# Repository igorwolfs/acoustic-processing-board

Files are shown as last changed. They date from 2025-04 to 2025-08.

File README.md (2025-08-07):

# acoustic-processing-hw
Repository for the main FPGA-processing board of my acoustic characterization device.

## Design goal
The goal of the board is to 
1. Measure analog signals amplified by a [pre-amplifier board](https://github.com/igorwolfs/acoustic-preamp-hw) for signals picked up from the piezo, at frequencies between 0.1 and 10 MHz. These analog signals are stored in RAM after measurement, processed on the FPGA and passed on.
2. Drive PWM signals for a [single-phase inverter-board](https://github.com/igorwolfs/acoustic-piezodriver-hw) connected to a piezo-element.

## Design constraints
Apart from technical constraints such as sampling rate (> 20 MHz), transfer / processing speed (10-bit x 35 MHz), etc... The main design constraint was keeping the price as low as possible.

## Stackup / Routing
6-layer stackup (JLC06161H-3313) with 
- L1, L6: controlled impedance layers.
	- 50 Ohm non-coplanar microstrip: 
		- TL Width (W): 0.157 mm 
		- Spacing between conductors: 2-3 x W
	- 100 Ohm differential non-coplanar
		- TL width (W): 0.122 mm
		- Diff-pair spacing: 0.2032 mm
		- Conductor spacing: 2-3 x W
- L4: power plane:
	- +2V5 Auxiliary FPGA voltage
	- +1V35 LPDDR3 voltage
	- +1V2 ETH voltage
	- +3V3 digital
	- +3V3 analog
- L2, L3, L5: GND planes
	- L2 (L1 reference)
	- L3 (L4 reference)
	- L5 (L6 reference)

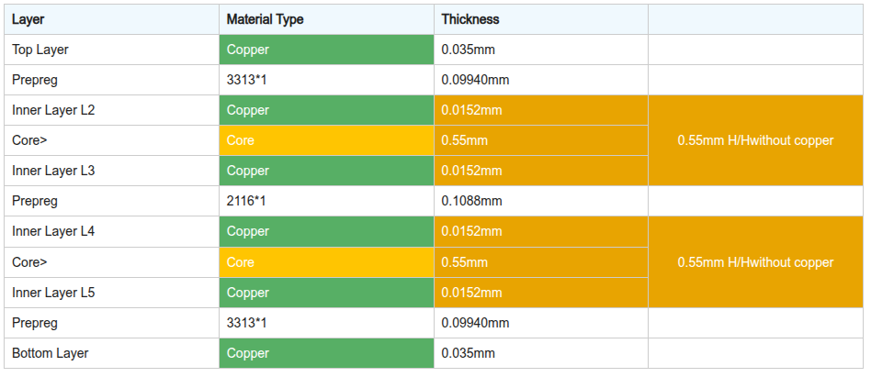
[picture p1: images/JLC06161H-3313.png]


### Rationale
Main reason for choosing a 6-layer over an 8-layer stack-up was price. Keeping LPDDR3-traces at appropriate impedance and matching delays proved to be a challenge with this layer count. Outcome to be judged after bringup.

## Main IC's
- Lattice EC5U-FPGA, with 25k LUT's.
- LPDDR3-RAM
- USB 33200-PHY (ULPI-bus)
- Ethernet PHY (RGMII interface)
- Analog frontend with MS9280 ADC in diff-mode, (fs <=35 MHz).

### Routing / Selection Rationale
#### Lattice ECP5U
The Lattice ECP5U was the best price-quality in terms of computing power. 

With a max CLK frequency of about 400 MHz it can operate around the lowest DDR3 speed class.

#### KSZ9031RN-Ethernet
Often used in open-source boards together with the ECP5U.

- RGMII interface operating at 125 MHz
- Differential pair needs to be tightly matched, offset calibration between pairs is performed.
- 4-pair RJ45 with intergrated magnetics (HR911130A)

#### Micron-DDR3 PHY
Anticipated was that around lower DDR3-speed classes (300 MHz, $\lambda = \frac{c}{300e6 * \sqrt{4.1}} = 50 cm$), delay-matching becomes less of an issue and higher ECP5U rise and fall times increase tolerance margin for the 50 ohm single-ended / 100 ohm differential impedance requirements.

- CMD-CTRL-bus 
	- signals led through vias twice.
	- CK+/- 42 mm
	- CMD/CTRL BUS signals kept around 35 mm (between 34-37 mm)
- DQU-group 
	- led through vias twice.
	- UDQS+/-: 21.7 mm
	- Data-signals kept within 1.5 mm
- DQL-group
	- signals kept on the first layer only.
	- LDQS+/-: 19.85 mm
	- Data-signals kept within 1.5 mm

 > References: [Orangecrab Board](https://github.com/orangecrab-fpga/orangecrab-hardware), Section 3.18 Lattice FPGA-DS-02012-3.2, [Micron DDR3 SDRAM](https://jlcpcb.com/api/file/downloadByFileSystemAccessId/8588894245961019392) table 58

#### USB3300-EZK
- ULPI-bus operating at 60 MHz
	- Traces were [delay-matched](docs/layout/USB/routing.md).
	- Impedance matched to 50 ohms.
- 2 Schmitt triggers were added for read-out of CC-line voltage to determine current USB PD capacity.

#### MS9280 ADC
Sampling rate > 2 times Nyquist, purchasing price was less than 1 $.

#### ADC RJ45 connectors + switch

2 RJ45 connectors meant to transfer analog signals attached with a switch. A comparison will be made for measuring analog signals between
- An RJ45 connector with internal magnetics.
- An RJ45 connector without magnetics, and with external blocking capacitors.
	- Capacitors might need to be changed, to stay out of S.R.F territory and limit phase-shift between differential signals.

#### W25Q128JVS SPI
2 external 128 MBit SPI IC's connected
- One to flash the ECP5U bitstream.
- One to flash firmware used in case of a soft-core CPU configured in the FPGA-fabric.

#### Other
More info on routing can be found in the (rather chaotic) [layout folder](docs/layout/) and [component selection folder](docs/schematic/component_selection/).

Simulations for ADI-devices can be found inside [ltspice-folder](simulations/ltspice/), TI-related sims can be found in the [TI-folder](simulations/TINA/)

## Booting
### Loading Bitstream 
2 possible ways of loading the bitstream of the ECP5U
- The JTAG-PMOD connector
- Flashing the external 128 MBit SPI connected to the startup MSPI of the ECP5U.

## Reviews
### Reddit
The first iteration of the design was placed on [reddit for review](https://www.reddit.com/r/PrintedCircuitBoard/comments/1m0hude/schematic_review_request_ecp5ufpga_board_with_hs/).

The initial design included longer trace-lengths to the DDR-PHY to achieve better delay and impedance matching. It was deemed that for the given stackup, sacrificing delay-budget and inter-trace distance wasn't worth the increase in trace lengths at those frequencies.

<table>
  <tr>
    <th>Before</th>
    <th>After</th>
  <tr>
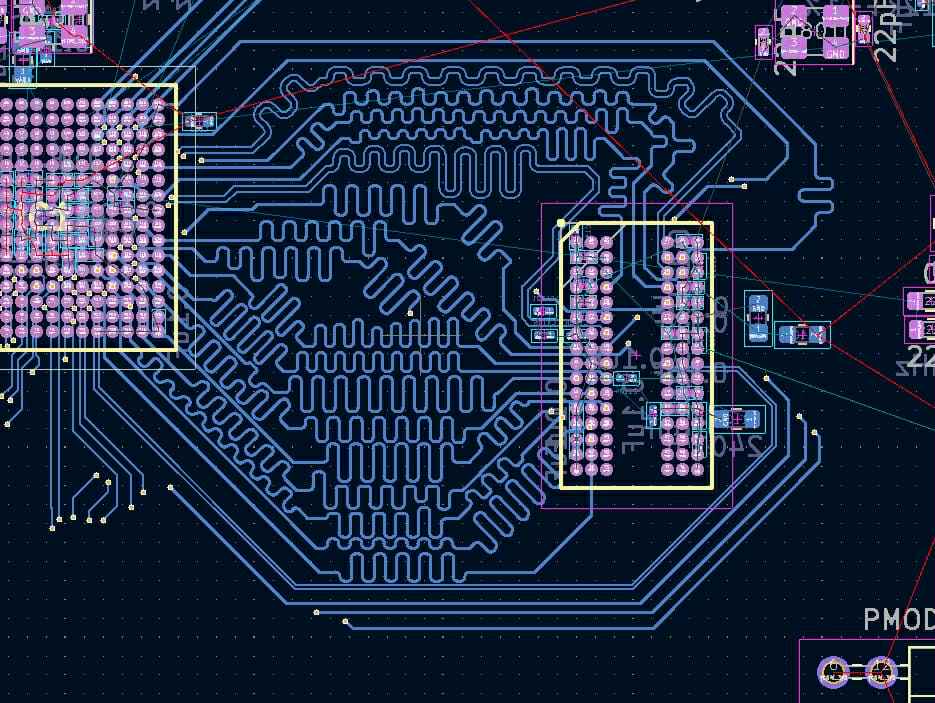
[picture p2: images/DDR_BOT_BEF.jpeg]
    <td> </td>
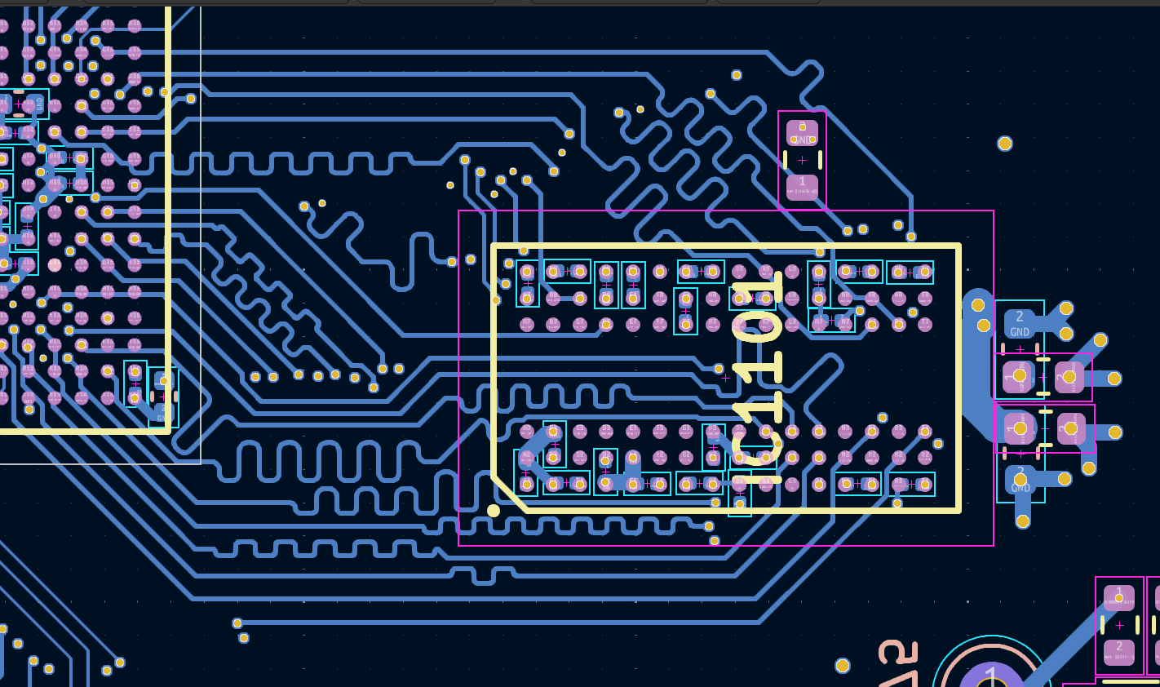
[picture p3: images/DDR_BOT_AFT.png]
    <td></td>
   </tr> 
   <tr>
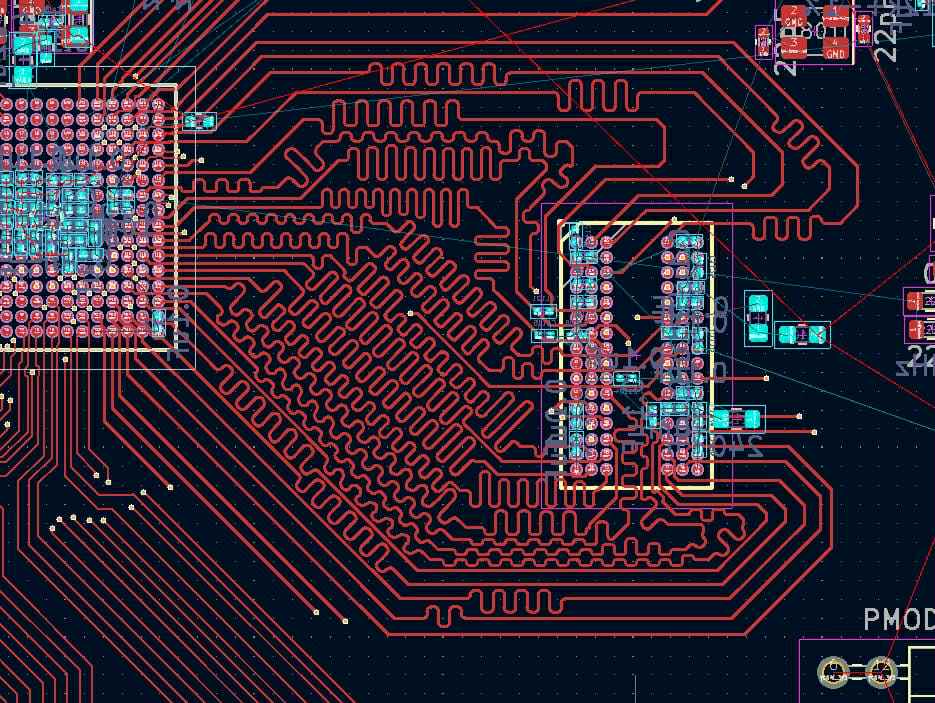
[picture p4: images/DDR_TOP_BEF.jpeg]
      <td></td>
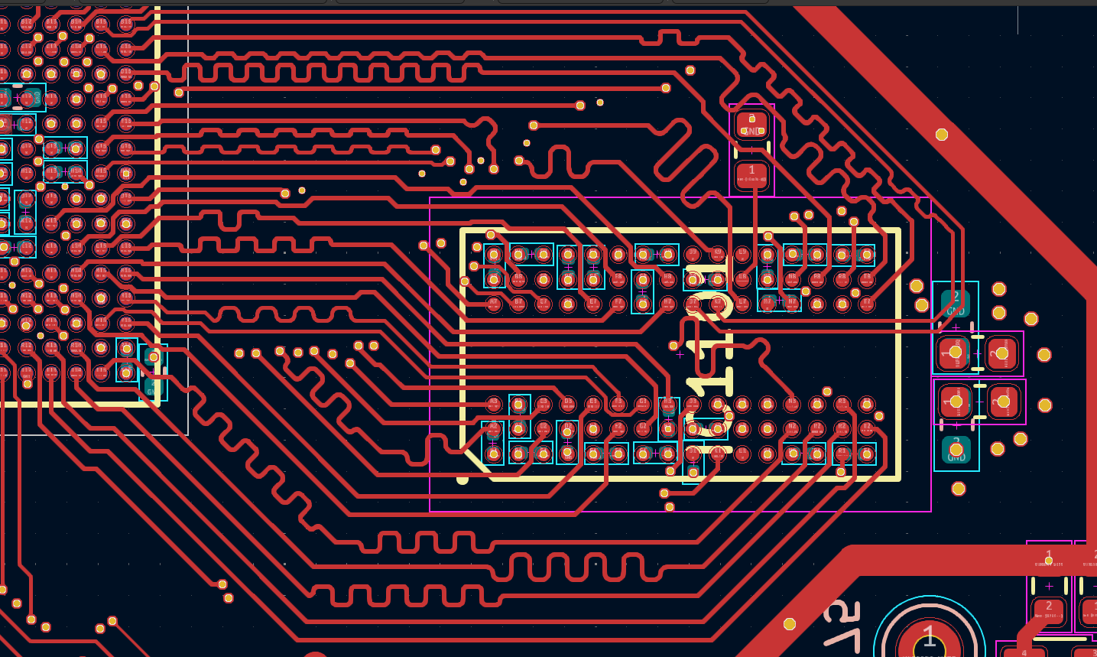
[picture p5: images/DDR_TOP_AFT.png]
      <td>
  </td>
</tr>
</table>

### Other
An additional LC-filter was added between shield and ground mostly for ESD-reasons.



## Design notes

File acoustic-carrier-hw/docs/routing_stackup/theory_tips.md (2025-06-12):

# Routing

## Signal Layer Changes
Make sure to add vias for high-speed signal so the return path can travel along a path of minimum impedance (so close to the signal path on a ground plane / power plane).

# Stackup
## Signal-Ground Separation
Planes that are further apart, have a higher impedance characteristics (so less capacitance, more inductance).
The fields have to spread so widely that EMI problems will be caused.

So for example, if plane 3-4 are spaced further apart, do not make one of those planes the reference GND plane.

Rules:
- 4-layer board: don't put power on 2, ground on 3
- 6-layer board: don't put power on 2, ground on 5

## Containing fields between SIG and PWR plane
### Why does it work?
a DC PWR plane is basically the same as a DC ground plane. The AC return current can flow on the power plane, induced by the signal on the SIG-plane. Then however this charge needs to find its way to a GND-plane, which it does through decouplign capacitors.

So although you can use a PWR plane as AC ground, the charge itself still needs to find its way to actual DC ground. 

So:

- The impedance to GND is slightly higher
- The decoupling between PWR and GND here is really important.
- Caps only decouple up to a certain frequency.
- If there is a split in the power plane, and a trace crosses a power plane, this will lead to massive impedances for the return path.
	- However in case of a closely spaced ground plane, the AC current can jump to the adjacent ground plane and continue to travel there.

### Solving the decoupling capacitor issue
- Placing a GND plane close, right next to the PWR plane creates a massive planar "capacitor" with a low-impedance AC-path between power and GND.

### FOR MORE CHECK OUT
- Transmission line theory / EM wave propagation
	- Modelling the trace as a distributed series inductance and shunt capacitance.
- Laws of EM: 
	- Boundary conditions for the wave equation in between 2 conductive geometries.

1. Signal changes rapidly (e.g.: from 0 -> 3.3 V)
2. Electric field changes rapidly in the dielectric between the signal and reference plane
3. This induces electric displacement field (D = eps * E)
4. (Amperes law) change in displacement field leads to change in magnetic field around the changing D-field
5. Surface current gets induced, which locally satisfies amperes law (induced on the reference plane)
	- Changing H field induces a voltage gradient
	- Voltage gradient causes electrons to move (conduction current)
	- This current is the AC return current.
6. **The AC induced return current together with the displacement current in the dielectric satisfy Ampere's law (with Maxwell's addition).** to generate the accompanying H-field.

## Power Ground Separation
Never put a power layer in a board without an adjacent GND plane.

### Q: WHY NOT?

## Good 6-layer stackups
### Stackup 1 - NOT cost effective
- POWER - SIG/GND
- CORE
- POWER - GND
- CORE 
- SIG/PWR - GND

Big CONS: 
- You have only 2 signal layers, for a 6 layer board.
- The signal needs to travel all the way from layer 1 to layer 6 in case of changing signal layers

### Stackup 2 - Better
- SIG/PWR - GND
- CORE
- SIG/PWR - GND
- CORE
- SIG/PWR - GND

Better: in this case the signal only needs to travel from layer 1->3 or 3->5.

# Sources:
- [LIVE] How to Achieve Proper Grounding - Rick Hartley - Expert Live Training (US), **Link:** https://www.youtube.com/watch?v=ySuUZEjARPY&ab_channel=Altium

- "Signal and Power Integrity - Simplified" (Book): THE foundational text for understanding these concepts practically. Chapter 4 (The Physical Basis of Transmission Lines)
- Key Paper: Bogatin, E. (1999). "No Myths Allowed! How Return Current Really Flows, and What to Do About It" (EDN Article)

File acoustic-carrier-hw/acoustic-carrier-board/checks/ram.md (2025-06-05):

# Decoupling
1.35 V
- Decoupling:
	- 3x22 uF
	- 2x10 uF
	- 1 uF
	- 0.1x10 uF
	- 2x10 nF
- Logicbone:
	- 5x0.1 uF
	- 4x10 uF
	- 47 uF

0.675
- Decoupling
	- 2x10 nF
	- 2x0.1 uF
- logicbone
	- 2x0.1 uF

VDDR_IO and VDDR_CORE are split with a ferrite
- both have 10 uF, 3x100 nF, 3x10nF capacitance

So more decoupling than logic bone, however no ferrite -> should be good though

Think about adding ferrites, check recommendations.

## Use a Ferrite:
- BLM18PG121SN1D
- DCR: 0.05 (is this acceptable) -> DCR for example schematic 

# DDR3 Connections
## DQ groups
- Pins UDM, UDQS, DQ15..8 should be on a bus together and length matched together
- Same with the lower dq-group

## Address group
- ADR [0:14], BA[0:2],CLK,CLK#,CLKE, WE#,CAS#,RAS#,CS#,ODT, RST should be drawn and matched together.

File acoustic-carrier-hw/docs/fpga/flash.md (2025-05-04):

# Flashing on FPGA
```
The flash voltage should match the VCCIO8 voltage.
It is recommended to use an SPI flash device that is supported in Diamond Programmer. To see the supported list of
devices, go to Diamond Programmer, under the Help menu, choose Help, then search for SPI Flash Support.
For SPI flash devices that are not listed in the SPI Flash Support, using the custom flash option may allow a nonsupported device to work.
```
Main reason seems to be the mathcing of Vcc_IO8 with the flash voltage.

## JTAG (VCCIO8)

### CFG
xxx
### Pins

- TDI, TMS, TDO (4.7 kOhm pullup)
- TCK (4.7 kOhm pulldown)

## SPI

Take the W25Q128JVSIQ

### SSPI (Slave SPI)

- CFG[2] = 0
- CFG[1] = 0
- CFG[0] = 1

### MSPI2 Configuring master SPI-port
To enable Master SPI configuration port, apply the settings below for the CFG pins on the ECP5/5G device:

Shared pins: 
- D[3:0], CSSPIN, DOUT

Dedicated pins
- PROGRAMN, INITN, DONE

#### cfg
- CFG[2] = 0
- CFG[1] = 1
- CFG[0] = 0

-> Configure this one by default, with connection of CFG_0 and CFG_1 to output so we can still change from SPI master to SPI slave if that were desired

# Example
## OrangeCrab
Orange Crab uses  W25Q128JVP (at 3.3 V), 128 M bit quad-spi NAND flash. (Serial NOR flash) / 16 MByte
- 128MBIT
- SPI_CONFIG_SS is pulled high.
	- So by default it is deselected
	- Probably pulled low by the FPGA
- D0..D3 floating

## ulx3
Uses IS25LP128F-JBLE flash (NOR Flash) / 16 MByte
- 128MBIT
- all spi pins are pulled high with a 4.7 kOhm resistor
	- Which is weird because it's push-pull, so except ofr the slave-select nothing should really be done.

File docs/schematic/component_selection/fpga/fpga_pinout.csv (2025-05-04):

# Pin Out For ECP5U-25
# Revision 1.1 - Include CABGA256 package
# Revised Oct. 17, 2017
# Revision 2.0 - Include TQFP144 package
# Revised Sep. 17, 2021
PAD | Pin/Ball Function | Bank | Dual Function | Differential | High Speed | DQS | CABGA381 | CSFBGA285 | CABGA256 | TQFP144
1 | PL2A | 7 | - | True_OF_PL2B | TRUE | LDQ8 | A4 | C12 | B1 | -
2 | PL2B | 7 | - | Comp_OF_PL2A | TRUE | LDQ8 | A5 | B12 | B2 | -
3 | VSSIO7 | - | - | - | - | - | - | - | - | -
4 | PL2C | 7 | - | True_OF_PL2D | - | LDQ8 | B5 | - | C3 | -
5 | VCCIO7 | - | - | - | - | - | - | - | - | -
6 | PL2D | 7 | - | Comp_OF_PL2C | - | LDQ8 | C5 | - | D3 | -
7 | PL5A | 7 | - | True_OF_PL5B | TRUE | LDQ8 | C4 | A12 | C1 | -
8 | VCCAUX | - | - | - | - | - | - | - | - | -
9 | PL5C | 7 | - | True_OF_PL5D | - | LDQ8 | A3 | - | E3 | 1
10 | PL5B | 7 | - | Comp_OF_PL5A | TRUE | LDQ8 | B4 | - | C2 | 3
11 | VSS | - | - | - | - | - | - | - | - | -
12 | PL5D | 7 | - | Comp_OF_PL5C | - | LDQ8 | B3 | - | F3 | 2
13 | PL8A | 7 | - | True_OF_PL8B | TRUE | LDQS8 | E4 | D13 | D1 | 4
14 | VCC | - | - | - | - | - | - | - | - | -
15 | PL8C | 7 | - | True_OF_PL8D | - | LDQ8 | C3 | - | F4 | 5
16 | PL8B | 7 | - | Comp_OF_PL8A | TRUE | LDQSN8 | D5 | C13 | E2 | 6
17 | VSS | - | - | - | - | - | - | - | - | -
18 | PL8D | 7 | - | Comp_OF_PL8C | - | LDQ8 | D3 | - | F5 | 7
19 | PL11A | 7 | - | True_OF_PL11B | TRUE | LDQ8 | F4 | - | G5 | -
20 | VSSIO7 | - | - | - | - | - | - | - | - | -
21 | PL11C | 7 | - | True_OF_PL11D | - | LDQ8 | E5 | - | F2 | -
22 | PL11B | 7 | - | Comp_OF_PL11A | TRUE | LDQ8 | E3 | - | G4 | -
23 | VCCIO7 | - | - | - | - | - | - | - | - | 9
24 | PL11D | 7 | - | Comp_OF_PL11C | - | LDQ8 | F5 | - | E1 | -
25 | PL14A | 7 | - | True_OF_PL14B | TRUE | LDQ20 | A2 | B13 | F1 | 10
26 | VSSIO7 | - | - | - | - | - | - | - | - | -
27 | PL14C | 7 | VREF1_7 | True_OF_PL14D | - | LDQ20 | B2 | C15 | G3 | 11
28 | PL14B | 7 | - | Comp_OF_PL14A | TRUE | LDQ20 | B1 | A13 | G2 | 12
29 | VCCIO7 | - | - | - | - | - | - | - | - | -
30 | PL14D | 7 | - | Comp_OF_PL14C | - | LDQ20 | C2 | A15 | H3 | 13
31 | PL17A | 7 | - | True_OF_PL17B | TRUE | LDQ20 | C1 | D15 | H5 | -
32 | VCCAUX | - | - | - | - | - | - | - | - | -
33 | PL17C | 7 | - | True_OF_PL17D | - | LDQ20 | D2 | - | J4 | -
34 | PL17B | 7 | - | Comp_OF_PL17A | TRUE | LDQ20 | D1 | D16 | H4 | -
35 | VSS | - | - | - | - | - | - | - | - | -
36 | PL17D | 7 | - | Comp_OF_PL17C | - | LDQ20 | E1 | - | J5 | -
37 | PL20A | 7 | GR_PCLK7_1 | True_OF_PL20B | TRUE | LDQS20 | H4 | B15 | G1 | -
38 | VCC | - | - | - | - | - | - | - | - | -
39 | PL20C | 7 | GR_PCLK7_0 | True_OF_PL20D | - | LDQ20 | H5 | C16 | J3 | -
40 | PL20B | 7 | - | Comp_OF_PL20A | TRUE | LDQSN20 | G5 | A16 | H2 | -
41 | VSS | - | - | - | - | - | - | - | - | -
42 | PL20D | 7 | - | Comp_OF_PL20C | - | LDQ20 | H3 | - | K3 | -
43 | PL23A | 7 | PCLKT7_1 | True_OF_PL23B | TRUE | LDQ20 | G3 | A17 | J1 | -
44 | VSSIO7 | - | - | - | - | - | - | - | - | -
45 | PL23C | 7 | PCLKT7_0 | True_OF_PL23D | - | LDQ20 | F2 | B18 | K1 | -
46 | PL23B | 7 | PCLKC7_1 | Comp_OF_PL23A | TRUE | LDQ20 | F3 | B17 | J2 | -
47 | VCCIO7 | - | - | - | - | - | - | - | - | -
48 | PL23D | 7 | PCLKC7_0 | Comp_OF_PL23C | - | LDQ20 | E2 | C17 | K2 | 14
49 | PL26A | 6 | PCLKT6_1 | True_OF_PL26B | TRUE | LDQ32 | G2 | D17 | L1 | -
50 | VSSIO6 | - | - | - | - | - | - | - | - | -
51 | PL26C | 6 | PCLKT6_0 | True_OF_PL26D | - | LDQ32 | H2 | D18 | M1 | -
52 | PL26B | 6 | PCLKC6_1 | Comp_OF_PL26A | TRUE | LDQ32 | F1 | C18 | L2 | -
53 | VCCIO6 | - | - | - | - | - | - | - | - | -
54 | PL26D | 6 | PCLKC6_0 | Comp_OF_PL26C | - | LDQ32 | G1 | F18 | M2 | -
55 | PL29A | 6 | GR_PCLK6_0 | True_OF_PL29B | TRUE | LDQ32 | J4 | F17 | K4 | -
56 | VCCAUX | - | - | - | - | - | - | - | - | -
57 | PL29C | 6 | GR_PCLK6_1 | True_OF_PL29D | - | LDQ32 | J3 | F15 | L4 | -
58 | PL29B | 6 | - | Comp_OF_PL29A | TRUE | LDQ32 | J5 | F16 | K5 | -
59 | VSS | - | - | - | - | - | - | - | - | -
60 | PL29D | 6 | - | Comp_OF_PL29C | - | LDQ32 | K3 | G16 | L5 | -
61 | PL32A | 6 | - | True_OF_PL32B | TRUE | LDQS32 | K2 | G18 | N1 | -
62 | VCC | - | - | - | - | - | - | - | - | -
63 | PL32C | 6 | - | True_OF_PL32D | - | LDQ32 | H1 | - | L3 | -
64 | PL32B | 6 | - | Comp_OF_PL32A | TRUE | LDQSN32 | J1 | H17 | P2 | 18
65 | VSS | - | - | - | - | - | - | - | - | -
66 | PL32D | 6 | - | Comp_OF_PL32C | - | LDQ32 | K1 | - | M3 | -
67 | PL35A | 6 | - | True_OF_PL35B | TRUE | LDQ32 | K4 | G15 | P1 | -
68 | VSSIO6 | - | - | - | - | - | - | - | - | -
69 | PL35C | 6 | - | True_OF_PL35D | - | LDQ32 | L4 | H16 | M4 | 22
70 | PL35B | 6 | VREF1_6 | Comp_OF_PL35A | TRUE | LDQ32 | K5 | H15 | R1 | 19
71 | VCCIO6 | - | - | - | - | - | - | - | - | -
72 | PL35D | 6 | - | Comp_OF_PL35C | - | LDQ32 | L5 | J16 | N3 | 23
73 | PL38A | 6 | - | True_OF_PL38B | TRUE | LDQ44 | M4 | - | N4 | 24
74 | VSSIO6 | - | - | - | - | - | - | - | - | -
75 | PL38C | 6 | - | True_OF_PL38D | - | LDQ44 | N4 | J17 | R2 | -
76 | PL38B | 6 | - | Comp_OF_PL38A | TRUE | LDQ44 | N5 | - | P3 | 25
77 | VCCIO6 | - | - | - | - | - | - | - | - | -
78 | PL38D | 6 | - | Comp_OF_PL38C | - | LDQ44 | P5 | H18 | T2 | -
79 | PL41A | 6 | - | True_OF_PL41B | TRUE | LDQ44 | N3 | J18 | P4 | -
80 | VCCAUX | - | - | - | - | - | - | - | - | -
81 | PL41C | 6 | - | True_OF_PL41D | - | LDQ44 | L3 | K16 | R4 | 26
82 | PL41B | 6 | - | Comp_OF_PL41A | TRUE | LDQ44 | M3 | K18 | R3 | -
83 | VSS | - | - | - | - | - | - | - | - | -
84 | PL41D | 6 | - | Comp_OF_PL41C | - | LDQ44 | L2 | K15 | T3 | 27
85 | PL44A | 6 | - | True_OF_PL44B | TRUE | LDQS44 | N2 | K17 | R5 | 28
86 | VCC | - | - | - | - | - | - | - | - | -
87 | PL44C | 6 | - | True_OF_PL44D | - | LDQ44 | L1 | L15 | M5 | 31
88 | PL44B | 6 | - | Comp_OF_PL44A | TRUE | LDQSN44 | M1 | L18 | T4 | 30
89 | VSS | - | - | - | - | - | - | - | - | -
90 | PL44D | 6 | - | Comp_OF_PL44C | - | LDQ44 | N1 | L16 | N5 | 33
91 | PL47A | 6 | - | True_OF_PL47B | TRUE | LDQ44 | P1 | - | M6 | 34
92 | VSSIO6 | - | - | - | - | - | - | - | - | 32
93 | PL47B | 6 | - | Comp_OF_PL47A | TRUE | LDQ44 | P2 | - | N6 | 35
94 | VCCIO6 | - | - | - | - | - | - | - | - | -
95 | PL47C | 6 | LLC_GPLL0T_IN | True_OF_PL47D | - | LDQ44 | P3 | M16 | P6 | 37
96 | PL47D | 6 | LLC_GPLL0C_IN | Comp_OF_PL47C | - | LDQ44 | P4 | M17 | P5 | -
97 | NC | - | - | - | - | - | - | - | - | -
98 | NC | - | - | - | - | - | - | - | - | -
99 | GND | - | - | - | - | - | - | - | - | -
100 | VCC | - | - | - | - | - | - | - | - | -
101 | VCC | - | - | - | - | - | - | - | - | -
102 | VSS | - | - | - | - | - | - | - | - | -
103 | PB4A | 8 | D7/IO7 | True_OF_PB4B | - | - | R1 | N15 | T6 | 40
104 | PB6A | 8 | D5/MISO2/IO5 | True_OF_PB6B | - | - | U1 | N17 | R7 | 39
105 | VCC | - | - | - | - | - | - | - | - | -
106 | PB4B | 8 | D6/IO6 | Comp_OF_PB4A | - | - | T1 | N16 | R6 | 44
107 | PB6B | 8 | D4/MOSI2/IO4 | Comp_OF_PB6A | - | - | V1 | M18 | P7 | 41
108 | VSS | - | - | - | - | - | - | - | - | -
109 | PB9A | 8 | D3/IO3 | True_OF_PB9B | - | - | W1 | N18 | N7 | 45
110 | PB11A | 8 | D1/MISO/IO1 | True_OF_PB11B | - | - | V2 | T18 | T7 | 46
111 | VSSIO8 | - | - | - | - | - | - | - | - | -
112 | PB9B | 8 | D2/IO2 | Comp_OF_PB9A | - | - | Y2 | R18 | M7 | -
113 | PB11B | 8 | D0/MOSI/IO0 | Comp_OF_PB11A | - | - | W2 | U18 | T8 | 47
114 | VCCIO8 | - | - | - | - | - | - | - | - | 43
115 | PB13A | 8 | SN/CSN | True_OF_PB13B | - | - | T2 | R17 | R8 | 48
116 | PB15A | 8 | HOLDN/DI/BUSY/CSSPIN/CEN | True_OF_PB15B | - | - | R2 | U17 | N8 | 49
117 | VSSIO8 | - | - | - | - | - | - | - | - | -
118 | PB13B | 8 | CS1N | Comp_OF_PB13A | - | - | U2 | T17 | P8 | 50
119 | PB15B | 8 | DOUT/CSON | Comp_OF_PB15A | - | - | R3 | V17 | M8 | 51
120 | VCCIO8 | - | - | - | - | - | - | - | - | -
121 | PB18A | 8 | WRITEN | - | - | - | T3 | R16 | M9 | 52
122 | INITN | 8 | - | - | - | - | V3 | V16 | T9 | 55
123 | VCCAUX | - | - | - | - | - | - | - | - | -
124 | CCLK | 8 | MCLK/SCK | - | - | - | U3 | U16 | N9 | 54
125 | PROGRAMN | 8 | - | - | - | - | W3 | T15 | R9 | 57
126 | VSS | - | - | - | - | - | - | - | - | -
127 | DONE | 8 | - | - | - | - | Y3 | U15 | P9 | 56
128 | CFG_1 | 8 | - | - | - | - | T4 | T14 | P10 | 59
129 | VCC | - | - | - | - | - | - | - | - | -
130 | CFG_2 | 8 | - | - | - | - | R4 | V15 | R10 | 58
131 | CFG_0 | 8 | - | - | - | - | U4 | U14 | N10 | 62
132 | VSS | - | - | - | - | - | - | - | - | -
133 | TDO | 40 | - | - | - | - | V4 | V14 | M10 | 60
134 | TCK | 40 | - | - | - | - | T5 | U13 | T10 | 63
135 | VSSIO8 | - | - | - | - | - | - | - | - | -
136 | TDI | 40 | - | - | - | - | R5 | T13 | R11 | 61
137 | TMS | 40 | - | - | - | - | U5 | V13 | T11 | 64
138 | VCCIO8 | - | - | - | - | - | - | - | - | -
139 | VCC | - | - | - | - | - | - | - | - | -
140 | VCC | - | - | - | - | - | - | - | - | -
141 | VSS | - | - | - | - | - | - | - | - | -
142 | VSS | - | - | - | - | - | - | - | - | -
143 | VCC | - | - | - | - | - | - | - | - | -
144 | VCC | - | - | - | - | - | - | - | - | -
145 | GND | - | - | - | - | - | - | - | - | -
146 | GND | - | - | - | - | - | - | - | - | -
147 | RESERVED | - | - | - | - | - | W4 | V12 | - | -
148 | GND | - | - | - | - | - | T7 | U12 | - | -
149 | RESERVED | - | - | - | - | - | W5 | V11 | - | -
150 | GND | - | - | - | - | - | - | - | - | -
151 | GND | - | - | - | - | - | - | - | - | -
152 | GND | - | - | - | - | - | Y5 | V9 | - | -
153 | GND | - | - | - | - | - | - | - | - | -
154 | GND | - | - | - | - | - | T8 | U8 | - | -
155 | GND | - | - | - | - | - | Y6 | V8 | - | -
156 | GND | - | - | - | - | - | - | - | - | -
157 | GND | - | - | - | - | - | - | - | - | -
158 | GND | - | - | - | - | - | Y7 | V6 | - | -
159 | GND | - | - | - | - | - | - | - | - | -
160 | GND | - | - | - | - | - | T9 | U6 | - | -
161 | GND | - | - | - | - | - | Y8 | V5 | - | -
162 | GND | - | - | - | - | - | - | - | - | -
163 | GND | - | - | - | - | - | - | - | - | -
164 | RESERVED | - | - | - | - | - | W8 | V3 | - | -
165 | GND | - | - | - | - | - | T10 | T5 | - | -
166 | RESERVED | - | - | - | - | - | W9 | V2 | - | -
167 | GND | - | - | - | - | - | - | - | - | -
168 | GND | - | - | - | - | - | - | - | - | -
169 | RESERVED | - | - | - | - | - | W10 | - | - | -
170 | GND | - | - | - | - | - | - | - | - | -
171 | RESERVED | - | - | - | - | - | W11 | - | - | -
172 | GND | - | - | - | - | - | - | - | - | -
173 | GND | - | - | - | - | - | - | - | - | -
174 | GND | - | - | - | - | - | Y11 | U1 | - | -
175 | GND | - | - | - | - | - | - | - | - | -
176 | GND | - | - | - | - | - | Y12 | T1 | - | -
177 | VCC | - | - | - | - | - | - | - | - | -
178 | VSS | - | - | - | - | - | - | - | - | -
179 | VCC | - | - | - | - | - | - | - | - | -
180 | GND | - | - | - | - | - | - | - | - | -
181 | NC | - | - | - | - | - | - | - | - | -
182 | NC | - | - | - | - | - | - | - | - | -
183 | PR47D | 3 | LRC_GPLL0C_IN | Comp_OF_PR47C | - | RDQ44 | T17 | N1 | P12 | 68
184 | PR47C | 3 | LRC_GPLL0T_IN | True_OF_PR47D | - | RDQ44 | U16 | M1 | P11 | 69
185 | VCCIO3 | - | - | - | - | - | - | - | - | -
186 | PR47B | 3 | - | Comp_OF_PR47A | TRUE | RDQ44 | U17 | - | N11 | 67
187 | VSSIO3 | - | - | - | - | - | - | - | - | -
188 | PR47A | 3 | - | True_OF_PR47B | TRUE | RDQ44 | U18 | - | M11 | 71
189 | PR44D | 3 | - | Comp_OF_PR44C | - | RDQ44 | T18 | N2 | N12 | -
190 | VSS | - | - | - | - | - | - | - | - | -
191 | PR44B | 3 | - | Comp_OF_PR44A | TRUE | RDQSN44 | R18 | L1 | T13 | -
192 | PR44C | 3 | - | True_OF_PR44D | - | RDQ44 | U19 | M2 | M12 | 72
193 | VCC | - | - | - | - | - | - | - | - | -
194 | PR44A | 3 | - | True_OF_PR44B | TRUE | RDQS44 | T19 | K2 | R12 | -
195 | PR41D | 3 | - | Comp_OF_PR41C | - | RDQ44 | U20 | K1 | T14 | 73
196 | VSS | - | - | - | - | - | - | - | - | -
197 | PR41B | 3 | - | Comp_OF_PR41A | TRUE | RDQ44 | R20 | L3 | R14 | 76
198 | PR41C | 3 | - | True_OF_PR41D | - | RDQ44 | T20 | K3 | R13 | 74
199 | VCCAUX | - | - | - | - | - | - | - | - | -
200 | PR41A | 3 | - | True_OF_PR41B | TRUE | RDQ44 | P20 | M3 | P13 | 77
201 | PR38D | 3 | - | Comp_OF_PR38C | - | RDQ44 | P18 | N3 | T15 | -
202 | VCCIO3 | - | - | - | - | - | - | - | - | -
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

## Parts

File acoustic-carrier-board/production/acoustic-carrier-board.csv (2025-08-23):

Reference | Qty | Value | Footprint | LCSC Part Number | Manufacturing Part Number
C201 | 1 | 150uF | Capacitor_SMD:CP_Elec_8x6.2 | C2162244 | APXE160ARA151MH80G
C202,C225,C227,C228,C301,C302,C303,C304,C305,C306,C310,C311,C401,C402,C404,C405,C407,C501,C502,C508,C509,C510,C513,C601,C604,C606,C612,C613,C702,C704,C706,C708,C801,C807,C808,C809,C810,C811,C812,C816,C820,C821,C822,C1002,C1003,C1004,C1005,C1008,C1009,C1010,C1011,C1013,C1019,C1021,C1024,C1026,C1027,C1101,C1102,C1103,C1104,C1105,C1106,C1108,C1109,C1110,C1111,C1112,C1116,C1118,C1119,C1120,C1121,C1122,C1123,C1124,C1125,C1203,C1204,C1206,C1207,C1209,C1210,C1216,C1217,C1218,C1219,C1220,C1221,C1222,C1223,C1229 | 92 | 0.1uF | Capacitor_SMD:C_0201_0603Metric | C22435929 | CGA0201X7R104K160ET
C203,C209,C217,C219 | 4 | 10pF | Capacitor_SMD:C_0402_1005Metric | C32949 | CL05C100JB5NNNC
C204,C205,C206,C210,C211,C214,C215,C220,C221,C222,C307,C308,C309,C1001,C1006,C1007,C1023,C1202,C1205,C1208,C1215,C1224 | 22 | 10uF | Capacitor_SMD:C_0603_1608Metric | C19702 | CL10A106KP8NNNC
C207,C212,C216,C223,C1014 | 5 | 1uF | Capacitor_SMD:C_0805_2012Metric | C28323 | CL21B105KBFNNNE
C208,C213,C218,C224,C312,C403,C406,C503,C512,C603,C611,C701,C705,C707,C813,C814,C819 | 17 | 4.7uF | Capacitor_SMD:C_0402_1005Metric | C23733 | CL05A475MP5NRNC
C226,C507,C511,C602,C703,C802,C817,C825,C1022,C1025,C1114,C1115,C1211,C1212,C1213,C1214,C1225 | 17 | 10nF | Capacitor_SMD:C_0201_0603Metric | C285010 | 0201B103K250NT
C313,C1107,C1113 | 3 | 22uF | Capacitor_SMD:C_0603_1608Metric | C59461 | CL10A226MQ8NRNC
C803,C806,C1227,C1228 | 4 | 22pF | Capacitor_SMD:C_0402_1005Metric | C1555 | 0402CG220J500NT
C804,C805 | 2 | 220pF | Capacitor_SMD:C_0402_1005Metric | C1530 | 0402B221K500NT
C815 | 1 | 1nF | Capacitor_SMD:C_1206_3216Metric | C9196 | 1206B102K202NT
C1012,C1015,C1016 | 3 | 10pF | Capacitor_SMD:C_0603_1608Metric_Pad1.08x0.95mm_HandSolder | C1634 | CL10C100JB8NNNC
C1017,C1018,C1028,C1029,C1226 | 5 | 100 nF +-5% | Capacitor_SMD:C_0603_1608Metric_Pad1.08x0.95mm_HandSolder | C1591,C88136 | 0603B104J500NT,CL10B104KB8NNNC
C1020 | 1 | 220nF | Capacitor_SMD:C_0402_1005Metric | C16772 | CL05B224KO5NNNC
D201 | 1 | D_Zener | Diode_SMD:D_SOD-323_HandSoldering | C19077443 | BZT52C6V8S
D601,D602,D801,D802 | 4 | LED_RED | LED_SMD:LED_0603_1608Metric | C2286 | KT-0603R
D1201 | 1 | 1N4148WS | Diode_SMD:D_SOD-323 | C2128 | 1N4148WS
IC1 | 1 | ECP5-BGA256 | iw-fpga_mcu:BGA256C80P16X16_1400X1400X170 | C1521614 | LFE5U-25F-6BG256C
IC1101 | 1 | MT41K256M16TW-107_P | iw-memory:BGA96C80P9X16_800X1400X120 | C253882 | MT41K256M16TW-107:P
J702 | 1 | PMOD_JTAG | iw-connector:PMOD_Pinsocket | C2897426 | PM254-2-06-W-8.5
J703 | 1 | PMOD_SPI | iw-connector:PMOD_Pinsocket | C2897426 | PM254-2-06-W-8.5
J704 | 1 | PMOD_GPIO | iw-connector:PMOD_Pinsocket | C2897426 | PM254-2-06-W-8.5
J801 | 1 | TYPE-C-31-M-12 | Connector_USB:USB_C_Receptacle_HRO_TYPE-C-31-M-12 | C165948 | TYPE-C-31-M-12
J1001,J1002,J1003,J1004,J1005,J1006,J1008,J1009,J1010,J1011 | 10 | BWU.FL-IPEX1 | iw-connector:BWU.FL-IPEX1 | C5137195 | BWU.FL-IPEX1
J1007 | 1 | 8P8C_Shielded | Connector_RJ:RJ45_RCH_RC01937 | C708652 | RC01937
J1201 | 1 | HR911130A | iw-connector:RJ45-TH_HR911130A | C54408 | HR911130A
L201,L202,L203,L204 | 4 | 2.2uH | iw-inductor:L_Changjiang_FNR4018S | C28642347 | NR4018S2R2MT
L401,L801,L1001,L1101,L1102,L1201,L1202,L1203 | 8 | 120@100MHz | Inductor_SMD:L_0603_1608Metric | C285595 | UPB160805T-121Y-N
Q201 | 1 | AO3401A | Package_TO_SOT_SMD:SOT-23 | C15127 | AO3401A
R201,R202,R604,R606,R704,R705,R707,R1204,R1208,R1212,R1213 | 11 | 4.7k | Resistor_SMD:R_0402_1005Metric | C25900 | 0402WGF4701TCE
R203,R216,R225,R226 | 4 | 24k | Resistor_SMD:R_0603_1608Metric | C23352 | 0603WAF2402T5E
R204,R803,R811 | 3 | 100k | Resistor_SMD:R_0603_1608Metric_Pad0.98x0.95mm_HandSolder | C25803 | 0603WAF1003T5E
R205 | 1 | 27k | Resistor_SMD:R_0603_1608Metric | C22967 | 0603WAF2702T5E
R206,R212 | 2 | 22k | Resistor_SMD:R_0603_1608Metric | C31850 | 0603WAF2202T5E
R207,R227,R804,R805 | 4 | 5.1k | Resistor_SMD:R_0603_1608Metric | C23186 | 0603WAF5101T5E
R208,R209,R217,R301 | 4 | 0 | Resistor_SMD:R_0805_2012Metric_Pad1.20x1.40mm_HandSolder | C17477 | 0805W8F0000T5E
R210,R211,R213 | 3 | 100k | Resistor_SMD:R_0603_1608Metric | C25803 | 0603WAF1003T5E
R215 | 1 | 75k | Resistor_SMD:R_0603_1608Metric | C23242 | 0603WAF7502T5E
R218 | 1 | 30k | Resistor_SMD:R_0603_1608Metric | C22984 | 0603WAF3002T5E
R219,R223,R401,R815,R830,R1009,R1013,R1021,R1024,R1030,R1031,R1032 | 12 | 1k | Resistor_SMD:R_0603_1608Metric | C21190 | 0603WAF1001T5E
R221,R602,R817,R1014,R1039 | 5 | 0 | Resistor_SMD:R_0603_1608Metric | C21189 | 0603WAF0000T5E
R222,R801 | 2 | 220 | Resistor_SMD:R_0603_1608Metric | C22962 | 0603WAF2200T5E
R601,R603,R605,R607,R701 | 5 | 470 | Resistor_SMD:R_0402_1005Metric | C25117 | 0402WGF4700TCE
R706,R1205 | 2 | 1k | Resistor_SMD:R_0402_1005Metric | C11702 | 0402WGF1001TCE
R802,R812 | 2 | 3k9 | Resistor_SMD:R_0603_1608Metric_Pad0.98x0.95mm_HandSolder | C23018 | 0603WAF3901T5E
R806 | 1 | 1M | Resistor_SMD:R_0402_1005Metric | C26083 | 0402WGF1004TCE
R807,R1012,R1015,R1017,R1018,R1020,R1201 | 7 | 0 | Resistor_SMD:R_0402_1005Metric_Pad0.72x0.64mm_HandSolder | C17168 | 0402WGF0000TCE
R808,R1202 | 2 | 12k+-1% | Resistor_SMD:R_0603_1608Metric | C22790 | 0603WAF1202T5E
R809,R810 | 2 | 33k | Resistor_SMD:R_0603_1608Metric | C4216 | 0603WAF3302T5E
R813,R821,R1016,R1019 | 4 | 47 | Resistor_SMD:R_0603_1608Metric | C23182 | 0603WAF470JT5E
R814,R826,R1038 | 3 | 4.7k | Resistor_SMD:R_0603_1608Metric | C23162 | 0603WAF4701T5E
R816 | 1 | 56k | Resistor_SMD:R_0603_1608Metric_Pad0.98x0.95mm_HandSolder | C23206 | 0603WAF5602T5E
R818 | 1 | 9k1 | Resistor_SMD:R_0603_1608Metric_Pad0.98x0.95mm_HandSolder | C23260 | 0603WAF9101T5E
R1001 | 1 | 0 | Resistor_SMD:R_0603_1608Metric_Pad0.98x0.95mm_HandSolder | C21189 | 0603WAF0000T5E
R1002,R1003,R1004,R1005,R1206,R1209 | 6 | 470 | Resistor_SMD:R_0603_1608Metric | C23179 | 0603WAF4700T5E
R1006,R1010,R1023,R1027,R1028,R1029,R1207,R1210,R1211 | 9 | 10k | Resistor_SMD:R_0603_1608Metric | C25804 | 0603WAF1002T5E
R1033 | 1 | 75 | Resistor_SMD:R_0603_1608Metric | C4275 | 0603WAF750JT5E
R1035 | 1 | 1k5 | Resistor_SMD:R_0603_1608Metric | C22843 | 0603WAF1501T5E
R1101 | 1 | 240 | Resistor_SMD:R_0603_1608Metric | C23350 | 0603WAF2400T5E
RJ1001 | 1 | HR913550A | iw-connector:RJ45-TH_HR913550A | C163507 | HR913550A
RN703,RN704,RN708,RN1201 | 4 | 4x4k7 | Resistor_SMD:R_Array_Convex_4x0603 | C1980 | 4D03WGJ0472T5E
RN707 | 1 | 4x10k | Resistor_SMD:R_Array_Convex_4x0603 | C29718 | 4D03WGJ0103T5E
SW602,SW603,SW701 | 3 | SW_Push | iw-misc:SW_TS-1088-AR02016 | C720477 | TS-1088-AR02016
U201 | 1 | TPS2121RUX | iw-power:TPS2121 | C2156025 | TPS2121RUXT
U202,U203,U204,U205 | 4 | TLV62569DBV | Package_TO_SOT_SMD:SOT-23-5 | C141836 | TLV62569DBVR
U206 | 1 | OPA376xxDBV | Package_TO_SOT_SMD:SOT-23-5 | C42134 | OPA376AIDBVR
U701,U702 | 2 | W25Q128JVS | Package_SO:SOIC-8_5.3x5.3mm_P1.27mm | C113767 | W25Q128JVSIQ
U801 | 1 | USB3300-EZK | iw-phyctrl:QFN32_5X5MC_MCH | C108383 | USB3300-EZK-TR
U802,U1004 | 2 | LMV321 | Package_TO_SOT_SMD:SOT-23-5 | C7972 | LMV321IDBVR
U803,U804 | 2 | ~ | Package_TO_SOT_SMD:SOT-23-5 | C3035955 | COS3201TR
U1001 | 1 | MS9280 | Package_SO:SSOP-28_5.3x10.2mm_P0.65mm | C1509021 | MS9280
U1002 | 1 | THS4521IDGK | Package_SO:VSSOP-8_3x3mm_P0.65mm | C170157 | THS4521IDGKR
U1003 | 1 | DGQ2788AEN-T1-GE4 | iw-analog:QFN40P260X180X60-16N_Fv1.2 | C2673179 | DGQ2788AEN-T1-GE4
U1005 | 1 | TL432DBZ | Package_TO_SOT_SMD:SOT-23 | C5184435 | TL432
U1201 | 1 | KSZ9031RN | Package_DFN_QFN:QFN-48-1EP_7x7mm_P0.5mm_EP5.15x5.15mm | C461575 | KSZ9031RNXCC
Y401 | 1 | Crystal Oscillator | Crystal:Crystal_SMD_3225-4Pin_3.2x2.5mm | C496694 | O93225100MEDA4SI-13
Y801 | 1 | Crystal_GND24_Small | Crystal:Crystal_SMD_3225-4Pin_3.2x2.5mm | C15643 | X322524MSB4SI
Y1201 | 1 | 25MHz | Crystal:Crystal_SMD_3225-4Pin_3.2x2.5mm | C9006 | X322525MOB4SI

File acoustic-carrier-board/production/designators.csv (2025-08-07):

C1001:1
C1002:1
C1003:1
C1004:1
C1005:1
C1006:1
C1007:1
C1008:1
C1009:1
C1010:1
C1011:1
C1012:1
C1013:1
C1014:1
C1015:1
C1016:1
C1017:1
C1018:1
C1019:1
C1020:1
C1021:1
C1022:1
C1023:1
C1024:1
C1025:1
C1026:1
C1027:1
C1028:1
C1029:1
C1101:1
C1102:1
C1103:1
C1104:1
C1105:1
C1106:1
C1107:1
C1108:1
C1109:1
C1110:1
C1111:1
C1112:1
C1113:1
C1114:1
C1115:1
C1116:1
C1118:1
C1119:1
C1120:1
C1121:1
C1122:1
C1123:1
C1124:1
C1125:1
C1202:1
C1203:1
C1204:1
C1205:1
C1206:1
C1207:1
C1208:1
C1209:1
C1210:1
C1211:1
C1212:1
C1213:1
C1214:1
C1215:1
C1216:1
C1217:1
C1218:1
C1219:1
C1220:1
C1221:1
C1222:1
C1223:1
C1224:1
C1225:1
C1226:1
C1227:1
C1228:1
C1229:1
C201:1
C202:1
C203:1
C204:1
C205:1
C206:1
C207:1
C208:1
C209:1
C210:1
C211:1
C212:1
C213:1
C214:1
C215:1
C216:1
C217:1
C218:1
C219:1
C220:1
C221:1
C222:1
C223:1
C224:1
C225:1
C226:1
C227:1
C228:1
C301:1
C302:1
C303:1
C304:1
C305:1
C306:1
C307:1
C308:1
C309:1
C310:1
C311:1
C312:1
C313:1
C401:1
C402:1
C403:1
C404:1
C405:1
C406:1
C407:1
C408:1
C501:1
C502:1
C503:1
C507:1
C508:1
C509:1
C510:1
C511:1
C512:1
C513:1
C601:1
C602:1
C603:1
C604:1
C606:1
C611:1
C612:1
C613:1
C701:1
C702:1
C703:1
C704:1
C705:1
C706:1
C707:1
C708:1
C801:1
C802:1
C803:1
C804:1
C805:1
C806:1
C807:1
C808:1
C809:1
C810:1
C811:1
C812:1
C813:1
C814:1
C815:1
C816:1
C817:1
C819:1
C820:1
C821:1
C822:1
C825:1
D1201:1
D201:1
D601:1
D602:1
D801:1
D802:1
FID101:1
FID102:1
FID103:1
FID104:1
FID105:1
FID106:1
FID107:1
FID108:1
H101:1
H102:1
H103:1
IC1:1
IC1101:1
J1001:1
J1002:1
J1003:1
J1004:1
J1005:1
J1006:1
J1007:1
J1008:1
J1009:1
J1010:1
J1011:1
J1201:1
J201:1
J701:1
J702:1
J703:1
J704:1
J801:1
J903:1
JP1001:1
JP1002:1
JP1003:1
JP1004:1
JP1005:1
JP1006:1
JP1007:1
JP1008:1
JP1009:1
JP1010:1
L1001:1
L1101:1
L1102:1
L1201:1
L1202:1
L1203:1
L201:1
L202:1
L203:1
L204:1
L401:1
L801:1
Q201:1
R1001:1
R1002:1
R1003:1
R1004:1
R1005:1
R1006:1
R1007:1
R1008:1
R1009:1
R1010:1
R1011:1
R1012:1
R1013:1
R1014:1
R1015:1
R1016:1
R1017:1
R1018:1
R1019:1
R1020:1
R1021:1
R1022:1
R1023:1
R1024:1
R1025:1
R1026:1
R1027:1
R1028:1
R1029:1
R1030:1
R1031:1
R1032:1
R1033:1
R1034:1
R1035:1
R1036:1
R1037:1
R1038:1
R1039:1
R1043:1
R1101:1
R1201:1
R1202:1
R1203:1
R1204:1
R1205:1
R1206:1
R1207:1
R1208:1
R1209:1
R1210:1
R1211:1
R1212:1
R1213:1
R201:1
R202:1
R203:1
R204:1
R205:1
R206:1
R207:1
R208:1
R209:1
R210:1
R211:1
R212:1
R213:1
R215:1
R216:1
R217:1
R218:1
R219:1
R220:1
R221:1
R222:1
R223:1
R224:1
R225:1
R226:1
R227:1
R301:1
R401:1
R601:1
R602:1
R603:1
R604:1
R605:1
R606:1
R607:1
R701:1
R704:1
R705:1
R706:1
R707:1
R801:1
R802:1
R803:1
R804:1
R805:1
R806:1
R807:1
R808:1
R809:1
R810:1
R811:1
R812:1
R813:1
R814:1
R815:1
R816:1
R817:1
R818:1
R821:1
R826:1
R830:1
RJ1001:1
RN1201:1
RN703:1
RN704:1
RN707:1
RN708:1
SW602:1
SW603:1
SW701:1
TP1001:1
TP1005:1
TP1011:1
TP1012:1
TP202:1
TP205:1
TP206:1
TP207:1
TP208:1
TP209:1
TP210:1
TP801:1
U1001:1
U1002:1
U1003:1
U1004:1
U1005:1
U1201:1
U201:1
U202:1
U203:1
U204:1
U205:1
U206:1
U701:1
U702:1
U801:1
U802:1
U803:1
U804:1
Y1201:1
Y401:1
Y801:1

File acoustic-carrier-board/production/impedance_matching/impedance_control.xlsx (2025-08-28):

Signal Layer | Reference Layer | Impedance Type | Trace Width（mm) | Trace Spacing（mm) | Impedance(ohm)±10% | Position | Description
DDR3-IMPEDANCE MATCHING
L1 | L2 | Single-ended (Non coplanar) | 0.1565 |  | 50 | images/z50_l12_se_ddr3.png | All DQ and command control bus traces connected between the FPGA and the DDR3-chip except for the differential strobes, and the CLK+- signals
L6 | L5 | Single-ended (Non coplanar) | 0.1565 |  | 50 | images/z50_l65_se_ddr3.png | All DQ and command control bus traces connected between the FPGA and the DDR3-chip except for the differential strobes, and the CLK+- signals
L1 | L2 | differential (Non-coplanar) | 0.1217 | 0.2032 | 100 (differential) | images/z100_l12_diff_ddr3.png | All DQS strobes and CK+/- for the command control bus
L6 | L5 | differential (Non-coplanar) | 0.1217 | 0.2032 | 100 (differential) | images/z100_l65_diff_ddr3.png | All DQS strobes and CK+/- for the command control bus
ETHERNET-IMPEDANCE MATCHING
L1 | L2 | Single-ended (Non coplanar) | 0.1565 |  | 50 | images/z50_l12_se_eth.png | Ethernet RGMII interface matching to 50 ohms, top layer
L6 | L5 | Single-ended (Non coplanar) | 0.1565 |  | 50 | images/z50_l65_se_eth.png | Ethernet RGMII interface matching to 50 ohms, Bottom layer
L1 | L2 | differential (Non-coplanar) | 0.1217 | 0.2032 | 100 (differential) | images/z100_l12_diff_eth.png | Gbit ethernet differential pair matching to 100 ohms, top layer
L6 | L5 | differential (Non-coplanar) | 0.1217 | 0.2032 | 100 (differential) | images/z100_l65_diff_eth.png | Gbit ethernet differential pair matching to 100 ohms, bottom layer
USB-IMPEDANCE MATCHING
L1 | L2 | Single-ended (Non coplanar) | 0.1565 |  | 50 | images/z50_l12_se_usb.png | USB ULPI interface matching to 50 ohms, top layer
L6 | L5 | Single-ended (Non coplanar) | 0.1565 |  | 50 | images/z50_l65_se_usb.png | USB ULPI interface matching to 50 ohms, bottom layer
L1 | L2 | differential (Non-coplanar) | 0.1554 | 0.2032 | 90 (differential) | images/z100_l12_diff_usb.png | USB differential pair matching to 90 ohms, top layer
L6 | L5 | differential (Non-coplanar) | 0.1554 | 0.2032 | 90 (differential) | images/z100_l65_diff_usb.png | USB differential pair matching to 90 ohms, Bottom layer
ANALOG TRACES MPEDANCE MATCHING
L1 | L2 | differential (Non coplanar) | 0.1217 | 0.2032 | 100 (differential) | images/z100_l12_diff_analog.png | Analog differential pair matching to 100 ohms, top layer
NOTES
Signal Layer | Reference Layer | Impedance Type | Position | Notes
L6 | L5 | 50 ohms | images/change_ulpi_clk_trace.png | Please reroute this trace to ensure sufficient distance between top and bottom highlighted trace in the image.

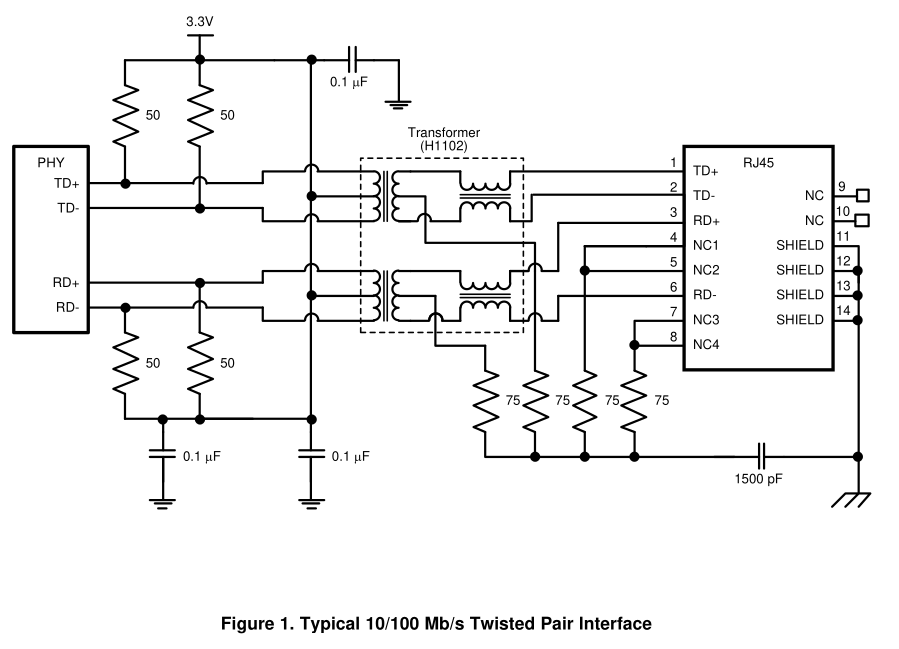
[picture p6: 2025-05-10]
docs/schematic/component_selection/ethernet/images/eth_phy.png

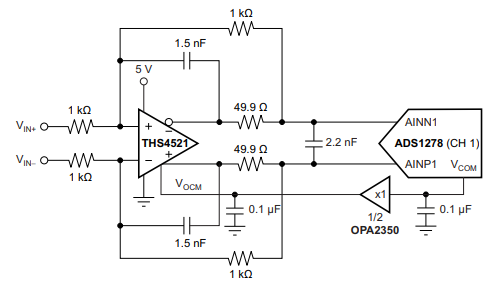
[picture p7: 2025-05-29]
docs/schematic/component_selection/adc/images/adc_buffer_example_circuit.png

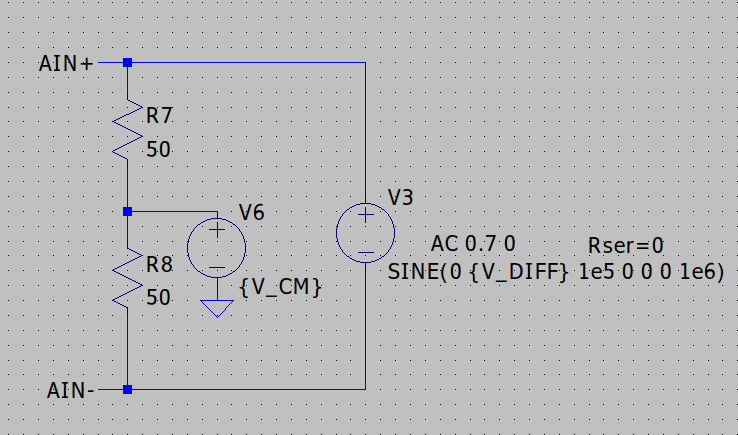
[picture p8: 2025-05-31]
docs/schematic/component_selection/adc/images/thevenin_diff_source.png

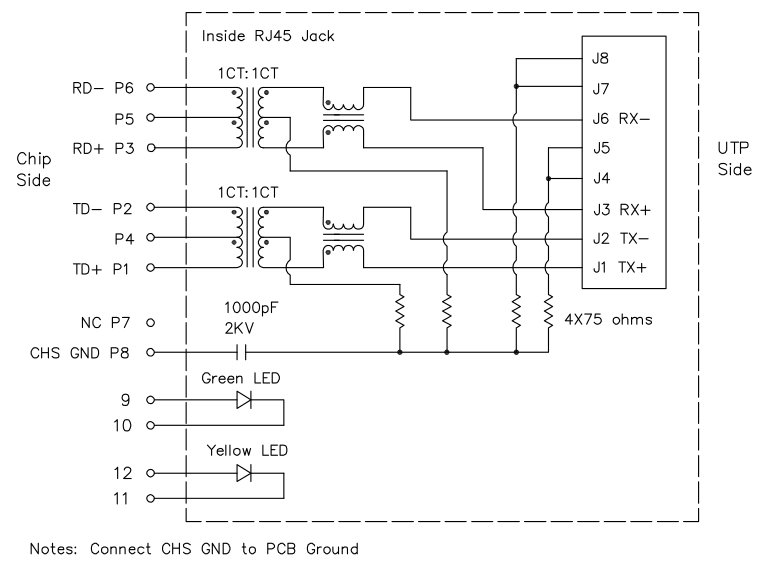
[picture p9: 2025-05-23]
docs/schematic/component_selection/ethernet/images/rj45_100Mb.png

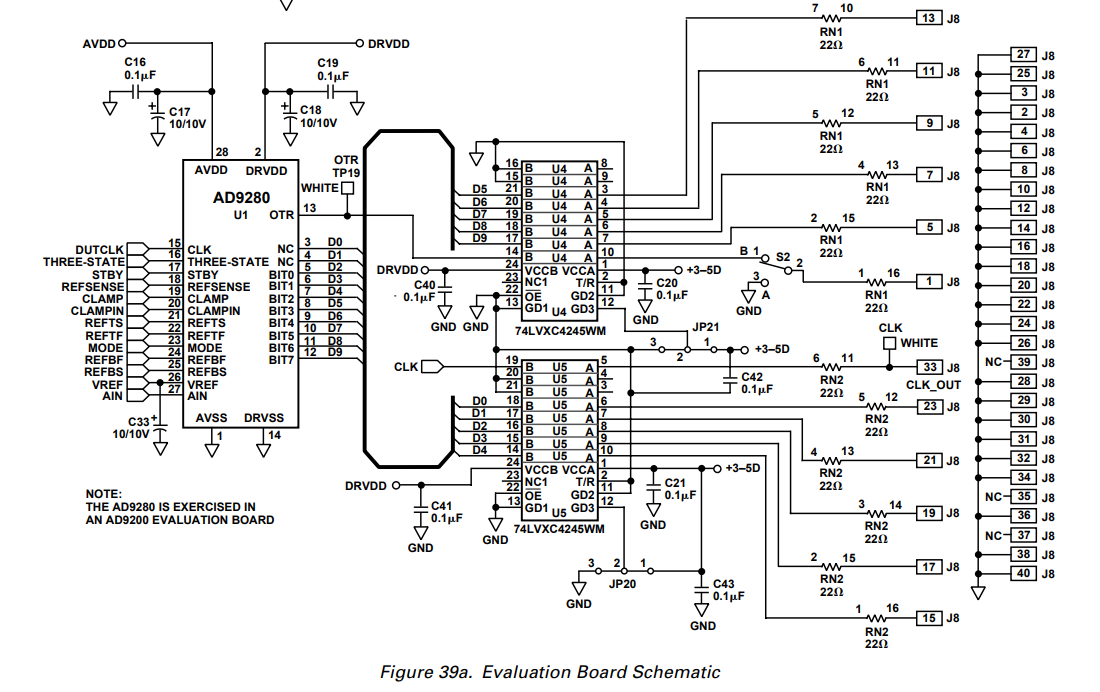
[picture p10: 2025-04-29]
docs/schematic/component_selection/adc/images/ms9280_AD9280.png

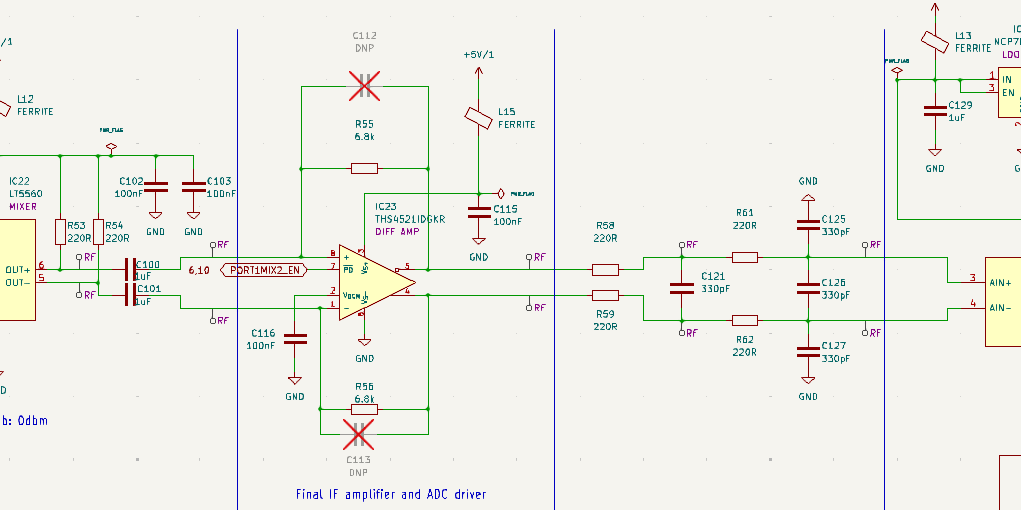
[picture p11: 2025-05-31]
docs/schematic/component_selection/adc/images/ths4521_vna.png

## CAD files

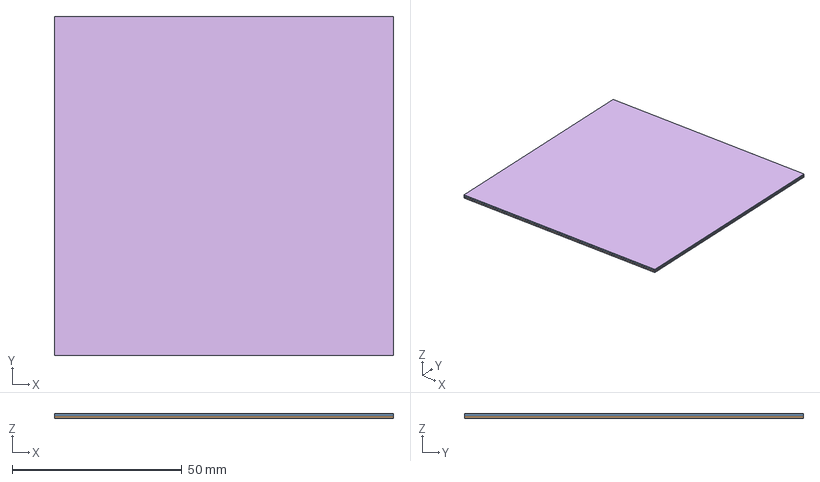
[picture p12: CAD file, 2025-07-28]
simulations/openEMS/impedance/freecad/JLC3313_6L/JLC3313_6L.FCStd
100.0 x 100.0 x 1.52 mm
L1_CU
L2_CU
L3_CU
L4_CU
L5_CU
L5_CU001
Prepreg_1
Prepreg_2
Prepreg_3
Core_1
Core_2

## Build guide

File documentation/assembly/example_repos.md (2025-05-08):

# Board mounting example repos
- PicoSat: Assembly of interconnected PCBs: https://github.com/Kmshanley/PicoSat-Initiative.git

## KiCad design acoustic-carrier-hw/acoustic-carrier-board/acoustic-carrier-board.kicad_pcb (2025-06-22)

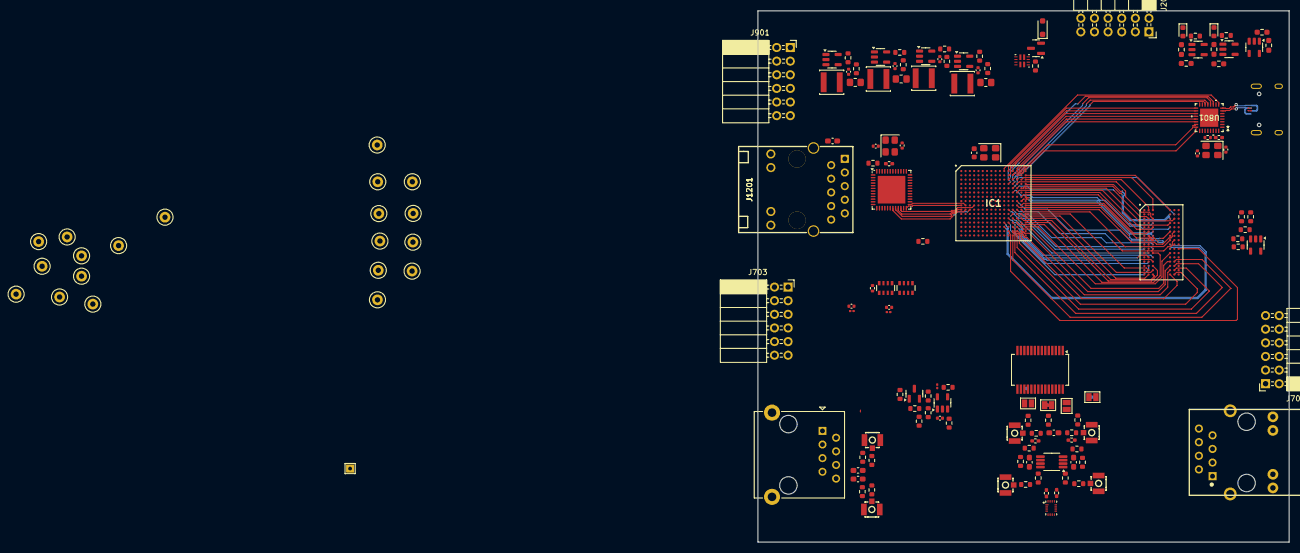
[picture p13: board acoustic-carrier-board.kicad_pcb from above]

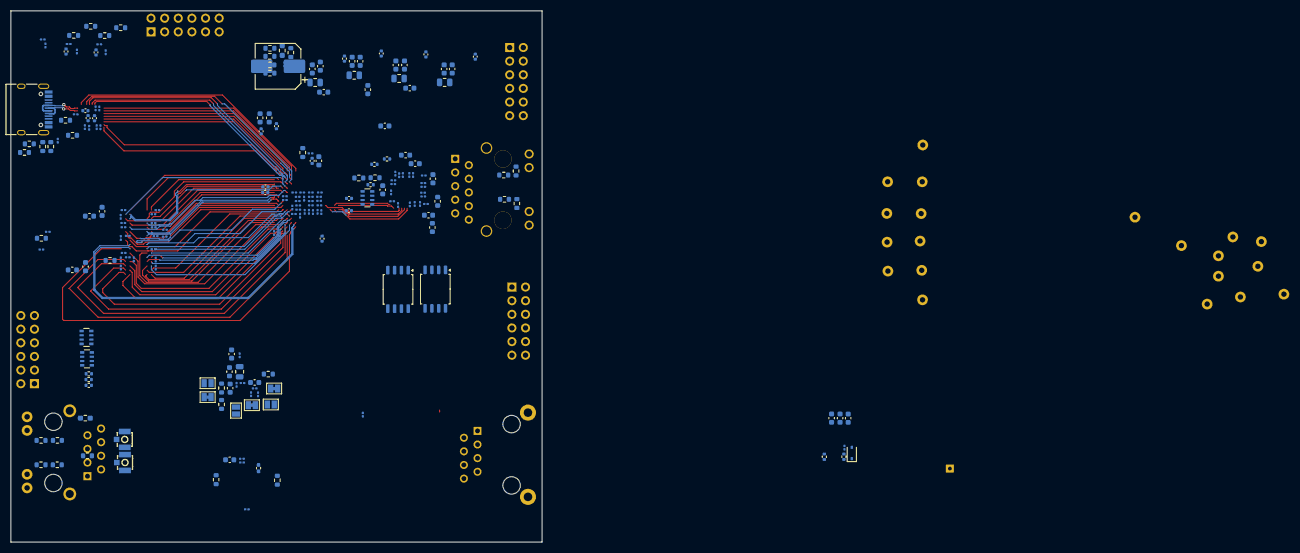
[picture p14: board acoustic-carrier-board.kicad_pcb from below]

Board: 6 copper layers, 99.0 x 99.0 mm, 361 parts (212 on the bottom side), 252 nets.

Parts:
C201: 150uF; CP_Elec_8x6.2
C202, C225, C301, C302, C303, C304, C305, C306, C310, C311, C401, C402, C404, C405, C407, C501, C502, C508, C509, C510, C513, C601, C612, C613, C702, C704, C706, C801, C807, C808, C809, C810, C811, C812, C816, C820, C821, C822, C1002, C1003, C1004, C1005, C1008, C1013, C1019, C1021, C1024, C1101, C1102, C1103, C1104, C1105, C1106, C1108, C1109, C1110, C1111, C1112, C1118, C1119, C1120, C1121, C1122, C1123, C1124, C1125, C1203, C1204, C1206, C1207, C1209, C1210, C1216, C1217, C1218, C1219, C1220, C1221, C1222, C1223, C1229: 0.1uF; C_0201_0603Metric
C203, C209, C217, C219: 10pF; C_0402_1005Metric
C204, C205, C206, C210, C211, C214, C215, C220, C221, C222, C307, C308, C309, C1001, C1006, C1007, C1023, C1202, C1205, C1208, C1215, C1224: 10uF; C_0603_1608Metric
C207, C212, C216, C223, C1014: 1uF; C_0805_2012Metric
C208, C213, C218, C224, C312, C403, C406, C503, C512, C603, C611, C701, C705, C707, C813, C814, C819: 4.7uF; C_0402_1005Metric
C226, C507, C511, C602, C703, C802, C817, C825, C1022, C1025, C1114, C1115, C1211, C1212, C1213, C1214, C1225: 10nF; C_0201_0603Metric
C313, C1107, C1113: 22uF; C_0603_1608Metric
C408: 5pF; C_0603_1608Metric
C803, C806, C1227, C1228: 22pF; C_0402_1005Metric
C804, C805: 220pF; C_0402_1005Metric
C1012, C1015, C1016: 10pF; C_0603_1608Metric_Pad1.08x0.95mm_HandSolder
C1017, C1018, C1226: 100 nF +-5%; C_0603_1608Metric_Pad1.08x0.95mm_HandSolder
C1020: 220nF; C_0402_1005Metric
D201: D_Zener; D_SOD-323_HandSoldering
D801, D802: LED_RED; LED_0603_1608Metric
D1201: 1N4148WS; D_SOD-323
IC1: ECP5-BGA256; BGA256C80P16X16_1400X1400X170
IC1101: MT41K256M16TW-107_P; BGA96C80P9X16_800X1400X120
J201, J701, J703, J901: Conn_02x06_Odd_Even; PinSocket_2x06_P2.54mm_Horizontal
J801: TYPE-C-31-M-12; USB_C_Receptacle_HRO_TYPE-C-31-M-12
J1001, J1002, J1003, J1005, J1006, J1008, J1009, J1010: BWU.FL-IPEX1
J1007: 8P8C_Shielded; RJ45_RCH_RC01937
J1201: HR911130A; RJ45-TH_HR911130A
JP1001, JP1004, JP1007, JP1008: SolderJumper_2_Bridged; SolderJumper-2_P1.3mm_Bridged_Pad1.0x1.5mm
JP1002, JP1003, JP1005, JP1006, JP1009, JP1010: SolderJumper_2_Open; SolderJumper-2_P1.3mm_Open_Pad1.0x1.5mm
L201, L202, L203, L204: 2.2uH; L_Changjiang_FNR4018S
L301, L501, L502, L1001, L1101, L1102, L1201, L1202, L1203: 120@100MHz; L_0603_1608Metric
Q201: AO3401A; SOT-23
R203, R216, R225, R226: 24k; R_0603_1608Metric
R204, R803, R811: 100k; R_0603_1608Metric_Pad0.98x0.95mm_HandSolder
R205: 27k; R_0603_1608Metric
R206, R212: 22k; R_0603_1608Metric
R207, R227, R804, R805: 5.1k; R_0603_1608Metric
R208, R209, R217: 0; R_0805_2012Metric_Pad1.20x1.40mm_HandSolder
R210, R211, R213: 100k; R_0603_1608Metric
R215: 75k; R_0603_1608Metric
R218: 30k; R_0603_1608Metric
R219, R223, R224, R401, R815, R830, R1009, R1013, R1021, R1024, R1030, R1031, R1032, R1034, R1036, R1037: 1k; R_0603_1608Metric
R220, R221, R602, R1007, R1008, R1011, R1014, R1022, R1025, R1026, R1039, R1043: 0; R_0603_1608Metric
R222, R801: 220; R_0603_1608Metric
R701, R702, R703, R1204, R1208, R1212, R1213: 4.7k; R_0402_1005Metric
R704, R1205: 1k; R_0402_1005Metric
R802, R812: 3k9; R_0603_1608Metric_Pad0.98x0.95mm_HandSolder
R806: 1M; R_0402_1005Metric
R807, R1012, R1015, R1017, R1018, R1020, R1201: 0; R_0402_1005Metric_Pad0.72x0.64mm_HandSolder
R808, R1202: 12k+-1%; R_0603_1608Metric
R809, R810: 33k; R_0603_1608Metric
R813, R821, R1016, R1019: 47; R_0603_1608Metric
R814, R826, R1038: 4.7k; R_0603_1608Metric
R816: 56k; R_0603_1608Metric_Pad0.98x0.95mm_HandSolder
R818: 9k1; R_0603_1608Metric_Pad0.98x0.95mm_HandSolder
R1001: 0; R_0603_1608Metric_Pad0.98x0.95mm_HandSolder
R1002, R1003, R1004, R1005, R1206, R1209: 470; R_0603_1608Metric
R1006, R1010, R1023, R1027, R1028, R1029, R1203, R1207, R1210, R1211: 10k; R_0603_1608Metric
R1033: 75; R_0603_1608Metric
R1035: 1k5; R_0603_1608Metric
R1101: 240; R_0603_1608Metric
RJ1001: HR913550A; RJ45-TH_HR913550A
RN701, RN702, RN704, RN1201: 4x4k7; R_Array_Convex_4x0603
RN703: 4x10k; R_Array_Convex_4x0603
TP202, TP203, TP205, TP206, TP207, TP208, TP209, TP210, TP801, TP804, TP807, TP1001, TP1004, TP1006, TP1007, TP1009, TP1010, TP1011, TP1012, TP1201: TestPoint; TestPoint_Loop_D1.80mm_Drill1.0mm_Beaded
TP1005: TestPoint; TestPoint_THTPad_1.5x1.5mm_Drill0.7mm
U201: TPS2121RUX; TPS2121
U202, U203, U204, U205: TLV62569DBV; SOT-23-5
U206: OPA376xxDBV; SOT-23-5
U701, U702: W25Q128JVS; SOIC-8_5.3x5.3mm_P1.27mm
U801: USB3300-EZK; QFN32_5X5MC_MCH
U802, U1004: LMV321; SOT-23-5
U803, U804: SOT-23-5
U1001: MS9280; SSOP-28_5.3x10.2mm_P0.65mm
U1002: THS4521IDGK; VSSOP-8_3x3mm_P0.65mm
U1003: DGQ2788AEN-T1-GE4; QFN40P260X180X60-16N_Fv1.2
U1005: TL432DBZ; SOT-23
U1201: KSZ9031RN; QFN-48-1EP_7x7mm_P0.5mm_EP5.15x5.15mm
Y401: Crystal Oscillator; Crystal_SMD_3225-4Pin_3.2x2.5mm
Y801: Crystal_GND24_Small; Crystal_SMD_3225-4Pin_3.2x2.5mm
Y1201: 25MHz; Crystal_SMD_3225-4Pin_3.2x2.5mm

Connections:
+1V2: C209.1, C210.1, C211.1, C212.1, L202.2, R209.1, R211.2, TP206.1
+1V35: C219.1, C220.1, C221.1, C222.1, C223.1, L204.2, R217.1, R218.2, TP209.1
+2V5: C214.1, C215.1, C216.1, C217.1, L203.2, L301.2, R215.2, TP207.1
+3V3: C203.1, C204.1, C205.1, C206.1, C207.1, L201.2, R208.1, R210.2, TP205.1
+5V: C201.1, C208.1, C213.1, C218.1, C224.1, TP202.1, U201.1 (OUT), U201.8 (OUT), U202.1 (EN), U202.4 (VIN), U203.1 (EN), U203.4 (VIN), U204.1 (EN), U204.4 (VIN), U205.1 (EN), U205.4 (VIN)
/ADC.CLK: IC1.P6 (PL47C/LLC_GPLL0T_IN), U1001.15 (CLK)
/ADC.D0: IC1.P5 (PL47D/LLC_GPLL0C_IN), U1001.3 (D0)
/ADC.D1: IC1.N6 (PL47B), U1001.4 (D1)
/ADC.D2: IC1.M6 (PL47A), U1001.5 (D2)
/ADC.D3: IC1.T3 (PL41D), U1001.6 (D3)
/ADC.D4: IC1.R4 (PL41C), U1001.7 (D4)
/ADC.D5: IC1.R3 (PL41B), U1001.8 (D5)
/ADC.D6: IC1.P4 (PL41A), U1001.9 (D6)
/ADC.D7: IC1.N5 (PL44D), U1001.10 (D7)
/ADC.D8: IC1.M5 (PL44C), U1001.11 (D8)
/ADC.D9: IC1.T4 (PL44B/LDQSN44), U1001.12 (D9)
/ADC.OTR: IC1.R5 (PL44A/LDQS44), U1001.13 (OTR)
/ANALOG-FRONTEND/ADC_AIN+: C1015.2, R1011.1, R1017.2, U1001.27 (AIN)
/ANALOG-FRONTEND/ADC_AIN-: C1015.1, R1014.1, R1020.2, R1022.1
/ANALOG-FRONTEND/ADC_MODE: JP1006.2 (B), JP1008.2 (B), JP1010.2 (B), TP1007.1, U1001.23 (MODE)
/ANALOG-FRONTEND/ADC_REFBF: C1001.2, C1002.2, C1004.1, U1001.24 (REFBF)
/ANALOG-FRONTEND/ADC_REFBS: JP1004.1 (A), JP1005.2 (B), TP1004.1, U1001.25 (REFBS)
/ANALOG-FRONTEND/ADC_REFSENSE: JP1007.2 (B), JP1009.2 (B), TP1006.1, U1001.18 (REFSENSE)
/ANALOG-FRONTEND/ADC_REFTF: C1001.1, C1002.1, C1003.1, U1001.22 (REFTF)
/ANALOG-FRONTEND/ADC_REFTS: JP1002.2 (B), JP1003.2 (B), JP1004.2 (B), R1014.2, U1001.21 (REFTS)
/ANALOG-FRONTEND/ADC_VDDA_2: JP1008.1 (A), R1030.2, R1031.1
/ANALOG-FRONTEND/ADC_VOCM_BUFF: C1020.2, R1006.1, R1010.1, R1023.1, R1027.1, R1028.1, R1029.2, R1033.1, R1039.1, TP1012.1, U1002.2 (V_{OCM})
/ANALOG-FRONTEND/ADC_VOCM_REF: C1022.1, R1032.2, R1034.2, R1035.1, R1037.1, TP1011.1, U1004.1 (+), U1005.2 (K)
/ANALOG-FRONTEND/ADC_VREF: C1013.1, C1014.1, JP1002.1 (A), JP1007.1 (A), U1001.26 (VREF)
/ANALOG-FRONTEND/MAG_ADC_AIN+: RJ1001.2, U1003.1 (NC2)
/ANALOG-FRONTEND/MAG_ADC_AIN-: RJ1001.1, U1003.13 (NC1)
/ANALOG-FRONTEND/RJ45_ADC_AIN+: C1018.2, R1008.1, R1029.1, U1003.15 (NO2)
/ANALOG-FRONTEND/RJ45_ADC_AIN-: C1017.2, R1027.2, R1043.1, U1003.11 (NO1)
/CON1.B40_EN: IC1.K5 (PL29B), J901.8
/CON1.PWM0: IC1.L1 (PL26A/LDQ32/PCLKT6_1), J901.1
/CON1.PWM1: IC1.L2 (PL26B/PCLKC6_1), J901.7
/CON1.PWM2: IC1.M1 (PL26C/PCLKT6_0), J901.11
/CON1.PWM3: IC1.M2 (PL26D/PCLKC6_0), J901.12
/CON1.S10V_EN: IC1.K4 (PL29A/GR_PCLK6_0), J901.10
/CON1.T_SCL: IC1.L4 (PL29C/PL29C), J901.6
/CON1.T_SDA: IC1.L5 (PL29D), J901.4
/DDR3/DDR3.A0: IC1.P14 (PR38B), IC1101.N3 (A0)
/DDR3/DDR3.A1: IC1.R15 (PR38C), IC1101.P7 (A1)
/DDR3/DDR3.A2: IC1.N16 (PR32A/RDQS32), IC1101.P3 (A2)
/DDR3/DDR3.A3: IC1.N13 (PR38A/RDQ44), IC1101.N2 (A3)
/DDR3/DDR3.A4: IC1.R13 (PR41C), IC1101.P8 (A4)
/DDR3/DDR3.A5: IC1.N12 (PR44D), IC1101.P2 (A5)
/DDR3/DDR3.A6: IC1.T14 (PR41D), IC1101.R8 (A6)
/DDR3/DDR3.A7: IC1.L16 (PR26A/PCLKT3_1/RDQ32), IC1101.R2 (A7)
/DDR3/DDR3.A8: IC1.P13 (PR41A), IC1101.T8 (A8)
/DDR3/DDR3.A9: IC1.L15 (PR26B/PCLKC3_1), IC1101.R3 (A9)
/DDR3/DDR3.A10: IC1.P16 (PR35A), IC1101.L7 (A10/AP)
/DDR3/DDR3.A11: IC1.R14 (PR41B), IC1101.R7 (A11)
/DDR3/DDR3.A12: IC1.P15 (PR32B/RDQSN32), IC1101.N7 (A12/BC#)
/DDR3/DDR3.A13: IC1.M15 (PR26D/PCLKC3_0), IC1101.T3 (A13)
/DDR3/DDR3.A14: IC1.T15 (PR38D), IC1101.T7 (A14)
/DDR3/DDR3.BA0: IC1.M12 (PR44C), IC1101.M2 (BA0)
/DDR3/DDR3.BA1: IC1.T13 (PR44B/RDQSN44), IC1101.N8 (BA1)
/DDR3/DDR3.BA2: IC1.M13 (PR35C), IC1101.M3 (BA2)
/DDR3/DDR3.CAS#: IC1.L14 (PR32C), IC1101.K3 (CAS#)
/DDR3/DDR3.CK+: IC1.P11 (PR47C/LRC_GPLL0T_IN), IC1101.J7 (CK)
/DDR3/DDR3.CK-: IC1.N11 (PR47B), IC1101.K7 (CK#)
/DDR3/DDR3.CKE: IC1.R12 (PR44A/RDQS44), IC1101.K9 (CKE)
/DDR3/DDR3.CS#: IC1.M14 (PR32D), IC1101.L2 (CS#)
/DDR3/DDR3.DQ0: IC1.F16 (PR14A/RDQ20), IC1101.E3 (DQ0)
/DDR3/DDR3.DQ1: IC1.J14 (PR20C/GR_PCLK2_1), IC1101.F7 (DQ1)
/DDR3/DDR3.DQ2: IC1.J15 (PR23B/PCLKC2_1), IC1101.F2 (DQ2)
/DDR3/DDR3.DQ3: IC1.K16 (PR23C/PCLKT2_0), IC1101.F8 (DQ3)
/DDR3/DDR3.DQ4: IC1.J16 (PR23A/PCLKT2_1), IC1101.H3 (DQ4)
/DDR3/DDR3.DQ5: IC1.K14 (PR20D/GR_PCLK2_0), IC1101.H8 (DQ5)
/DDR3/DDR3.DQ6: IC1.H14 (PR14D), IC1101.G2 (DQ6)
/DDR3/DDR3.DQ7: IC1.K15 (PR23D/PCLKC2_0/RDQ20), IC1101.H7 (DQ7)
/DDR3/DDR3.DQ8: IC1.F14 (PR5D), IC1101.D7 (DQ8)
/DDR3/DDR3.DQ9: IC1.D14 (PR2D), IC1101.C3 (DQ9)
/DDR3/DDR3.DQ10: IC1.E16 (PR11D/RDQ8), IC1101.C8 (DQ10)
/DDR3/DDR3.DQ11: IC1.E14 (PR5C), IC1101.C2 (DQ11)
/DDR3/DDR3.DQ12: IC1.B16 (PR2A/RDQ8), IC1101.A7 (DQ12)
/DDR3/DDR3.DQ13: IC1.C16 (PR5A), IC1101.A2 (DQ13)
/DDR3/DDR3.DQ14: IC1.C14 (PR2C), IC1101.B8 (DQ14)
/DDR3/DDR3.DQ15: IC1.C15 (PR5B), IC1101.A3 (DQ15)
/DDR3/DDR3.LDM: IC1.G15 (PR14B), IC1101.E7 (LDM)
/DDR3/DDR3.LDQS+: IC1.G16 (PR20A/RDQS20), IC1101.F3 (LDQS)
/DDR3/DDR3.LDQS-: IC1.H15 (PR20B/RDQSN20), IC1101.G3 (LDQS#)
/DDR3/DDR3.ODT: IC1.K12 (PR29B), IC1101.K1 (ODT)
/DDR3/DDR3.RAS#: IC1.K13 (PR29A/GR_PCLK3_0), IC1101.J3 (RAS#)
/DDR3/DDR3.RESET#: IC1.M16 (PR26C/PCLKT3_0), IC1101.T2 (RESET#)
/DDR3/DDR3.UDM: IC1.F13 (PR8C), IC1101.D3 (UDM)
/DDR3/DDR3.UDQS+: IC1.D16 (PR8A/RDQS8), IC1101.B7 (UDQS#)
/DDR3/DDR3.UDQS-: IC1.E15 (PR8B/RDQSN8), IC1101.C7 (UDQS)
/DDR3/DDR3.WE#: IC1.N14 (PR35D/RDQ32), IC1101.L3 (WE#)
/DDR3/VDDR_CORE: C1101.1, C1103.1, C1104.1, C1105.1, C1106.1, C1107.1, C1118.1, C1119.1, C1120.1, C1124.1, IC1101.B2 (VDD_1), IC1101.D9 (VDD_2), IC1101.G7 (VDD_3), IC1101.K2 (VDD_4), IC1101.K8 (VDD_5), IC1101.N1 (VDD_6), IC1101.N9 (VDD_7), IC1101.R1 (VDD_8), IC1101.R9 (VDD_9), L1101.1
/DDR3/VDDR_DQ: C1102.1, C1108.1, C1109.1, C1110.1, C1111.1, C1112.1, C1113.1, C1123.1, C1125.1, IC1101.A1 (VDDQ_1), IC1101.A8 (VDDQ_2), IC1101.C1 (VDDQ_3), IC1101.C9 (VDDQ_4), IC1101.D2 (VDDQ_5), IC1101.E9 (VDDQ_6), IC1101.F1 (VDDQ_7), IC1101.H2 (VDDQ_8), IC1101.H9 (VDDQ_9), L1102.1
/ETHERNET-PHY/ETH_AC_GND: C1226.1, J1201.1
/ETHERNET-PHY/ETH_GLED_K: J1201.12, R1206.1
/ETHERNET-PHY/ETH_LED_1: R1209.2, R1210.1, U1201.17 (LED1/PHAD0/PME_N1)
/ETHERNET-PHY/ETH_LED_2: R1206.2, R1207.1, U1201.15 (LED2/PHYAD1)
/ETHERNET-PHY/ETH_PHY_A+: J1201.2, U1201.2 (TXRXP_A)
/ETHERNET-PHY/ETH_PHY_A-: J1201.3, U1201.3 (TXRXM_A)
/ETHERNET-PHY/ETH_PHY_B+: J1201.4, U1201.5 (TXRXP_B)
/ETHERNET-PHY/ETH_PHY_B-: J1201.7, U1201.6 (TXRXM_B)
/ETHERNET-PHY/ETH_PHY_C+: J1201.5, U1201.7 (TXRXP_C)
/ETHERNET-PHY/ETH_PHY_C-: J1201.6, U1201.8 (TXRXM_C)
/ETHERNET-PHY/ETH_PHY_D+: J1201.8, U1201.10 (TXRXP_D)
/ETHERNET-PHY/ETH_PHY_D-: J1201.9, U1201.11 (TXRXM_D)
/ETHERNET-PHY/ETH_YLED_K: J1201.13, R1209.1
/ETHERNET-PHY/VDDAH_3V3: C1202.1, C1203.1, C1204.1, L1203.2, U1201.1 (AVDDH), U1201.12 (AVDDH)
/ETHERNET-PHY/VDDAL_1V2: C1208.1, C1209.1, C1210.1, C1211.1, C1212.1, L1201.1, U1201.4 (AVDDL), U1201.9 (AVDDL)
/ETHERNET-PHY/VDDAPLL_1V2: C1205.1, C1206.1, C1207.1, L1202.1, U1201.44 (AVDDL_PLL)
/FPGA-CONFIG-FLASH/FPGA_CFG0: IC1.N10 (CFG0), J701.12, R702.1
/FPGA-CONFIG-FLASH/FPGA_CFG1: IC1.P10 (CFG1), J701.11, RN702.1 (R1.1)
/FPGA-CONFIG-FLASH/FPGA_CFG2: IC1.R10 (CFG2), J701.9, R703.2
/FPGA-CONFIG-FLASH/FPGA_DONE: IC1.P9 (DONE), J701.7, RN702.2 (R2.1)
/FPGA-CONFIG-FLASH/FPGA_RESET: IC1.R9 (~PROGRAM), J701.3, RN702.4 (R4.1)
/FPGA-CONFIG-FLASH/JTAG.TCK: IC1.T10 (TCK), J701.6, R701.1
/FPGA-CONFIG-FLASH/JTAG.TDI: IC1.R11 (TDI), J701.8, RN701.2 (R2.1)
/FPGA-CONFIG-FLASH/JTAG.TDO: IC1.M10 (TDO), J701.10, RN701.3 (R3.1)
/FPGA-CONFIG-FLASH/JTAG.TMS: IC1.T11 (TMS), J701.4, RN701.1 (R1.1)
/FPGA-CONFIG-FLASH/QSPI.CSPPIn1: IC1.N8 (~HOLD/DI/BUSY/~CSSPI/PB15A), J703.8, RN704.3 (R3.1), U701.1 (~CS)
/FPGA-CONFIG-FLASH/QSPI.CSPPIn2: IC1.M8 (DOUT/~CSO/PB15B), J703.6, RN704.1 (R1.1), U702.1 (~CS)
/FPGA-CONFIG-FLASH/QSPI.CSn: IC1.R8 (~CS/~S/PB13A), J703.10, RN704.4 (R4.1)
/FPGA-CONFIG-FLASH/QSPI.D0: IC1.T8 (D0/PICO/IO0/PB11B), J703.12, RN703.1 (R1.1), U701.5 (DI/IO_{0}), U702.5 (DI/IO_{0})
/FPGA-CONFIG-FLASH/QSPI.D1: IC1.T7 (D1/POCI/IO1/PB11A), J703.11, RN703.2 (R2.1), U701.2 (DO/IO_{1}), U702.2 (DO/IO_{1})
/FPGA-CONFIG-FLASH/QSPI.D2: IC1.M7 (D2/IO2/PB9B), J703.9, RN703.3 (R3.1), U701.3 (~WP/IO_{2}), U702.3 (~WP/IO_{2})
/FPGA-CONFIG-FLASH/QSPI.D3: IC1.N7 (D3/IO3/PB9A), J703.7, RN703.4 (R4.1), U701.7 (~HOLD/~RESET/IO_{3}), U702.7 (~HOLD/~RESET/IO_{3})
/FPGA-CONFIG-FLASH/QSPI.MCLK: IC1.N9 (MCLK/SCK/CCLK), J703.4, R704.2, U701.6 (CLK), U702.6 (CLK)
/FPGA-CONFIG-FLASH/~FPGA_INIT: IC1.T9 (~INIT), J701.5, RN702.3 (R3.1)
/FPGA-DQBANK-23/VDDR_BANK2: C501.1, C502.1, C503.1, IC1.H11 (VCCIO2_1), IC1.J11 (VCCIO2_2), L501.1
/FPGA-DQBANK-23/VDDR_BANK3: C509.1, C510.1, C511.1, C512.1, IC1.K11 (VCCIO3_1), IC1.L11 (VCCIO3_2), L502.1
/FPGA-POWER/VAUX: C310.1, C311.1, C312.1, C313.1, IC1.G11 (VCCAUX_1), IC1.L7 (VCCAUX_2), L301.1
/POWER/BP_5V: D201.1 (K), J201.1, J201.3, J201.5, J201.7, J201.9, J201.11, Q201.2 (S)
/POWER/USB_VBUS: C801.1, C807.1, C808.1, C822.1, J801.A4 (VBUS), J801.A9 (VBUS), J801.B4 (VBUS), J801.B9 (VBUS), R226.1, R801.1, R809.1, R816.2, TP210.1, U201.2 (IN2), U802.5 (V+), U803.5 (V+), U804.5 (V+)
/RGMII_MDIO.DATA: R1205.1, U1201.37 (MDIO)
/RGMII_RX.CLK: R1203.2, R1211.1, U1201.35 (RX_CLK/PHYAD2)
/RGMII_RX.CTL: R1204.1, U1201.33 (RX_DV/CLK125_EN)
/RGMII_RX.D0: RN1201.1 (R1.1), U1201.32 (RXD0/MODE0)
/RGMII_RX.D1: RN1201.2 (R2.1), U1201.31 (RXD1/MODE1)
/RGMII_RX.D2: RN1201.3 (R3.1), U1201.28 (RXD2/MODE2)
/RGMII_RX.D3: RN1201.4 (R4.1), U1201.27 (RXD3/MODE3)
/RGMII_TX.CLK: IC1.J1 (PL23A/PCLKT7_1), U1201.24 (GTX_CLK)
/RGMII_TX.CTL: IC1.J2 (PL23B/PCLKC7_1), U1201.25 (TX_EN)
/RGMII_TX.D0: IC1.K3 (PL20D), U1201.19 (TXD0)
/RGMII_TX.D1: IC1.K2 (PL23D/PCLKC7_0/LDQ20), U1201.20 (TXD1)
/RGMII_TX.D2: IC1.K1 (PL23C/PCLKT7_0), U1201.21 (TXD2)
/RGMII_TX.D3: IC1.J4 (PL17C), U1201.22 (TXD3)
/USB-PHY/USBCC_VREF_BUFF: R802.1, R812.1, TP801.1, U802.3 (-), U802.4
/USB-PHY/USB_CC1: C805.1, J801.A5 (CC1), R805.2, U804.4 (-)
/USB-PHY/USB_CC2: C804.1, J801.B5 (CC2), R804.2, U803.4 (-)
/USB-PHY/USB_D+: J801.A6 (DP1), J801.B6 (DP2), U801.7 (DP)
/USB-PHY/USB_D-: J801.A7 (DN1), J801.B7 (DN2), U801.8 (DM)
/USB-PHY/VDDA_USB1V8: C814.1, C816.1, U801.29 (VDDA1.8)
/USB-PHY/VDD_USB1V8: C819.1, C820.1, C821.1, U801.15 (VDD1.8), U801.26 (VDD1.8)
/USB.CLK: IC1.E13 (PT62B), U801.14 (CLKOUT)
/USB.D0: IC1.B14 (PT67A), U801.24 (DATA0)
/USB.D1: IC1.A15 (PT67B), U801.23 (DATA1)
/USB.D2: IC1.B13 (PT60A), U801.22 (DATA2)
/USB.D3: IC1.A14 (PT65B), U801.21 (DATA3)
/USB.D4: IC1.C12 (PT56B), U801.20 (DATA4)
/USB.D5: IC1.A13 (PT65A), U801.19 (DATA5)
/USB.D6: IC1.B12 (PT56A), U801.18 (DATA6)
/USB.D7: IC1.A12 (PT53B), U801.17 (DATA7)
/USB.DIR: IC1.D13 (PT62A), U801.12 (DIR)
/USB.NXT: IC1.D12 (PT58A), U801.11 (NXT)
/USB.RST: IC1.A11 (PT53A), U801.9 (RESET)
/USB.STP: IC1.C13 (PT60B), U801.13 (STP)
ETH_REFCLK: IC1.G1 (PL20A/GR_PCLK7_1/LDQSN20), IC1.J3 (PL20C/GR_PCLK7_0), R1213.1, U1201.41 (CLK125_NDO/LED_MODE)
FPGA_ADC_LED0: IC1.R2 (PL38C), R1004.2, R1005.2
FPGA_ADC_LED1: IC1.P3 (PL38B), R1002.2, R1003.1
FPGA_ADC_SW: IC1.T2 (PL38D), TP1005.1, U1003.14 (IN1-2)
FPGA_CC1: IC1.E10 (PT47B), R814.1
FPGA_CC2: IC1.B11 (PT49A), R826.1
FPGA_USB_SENSE: IC1.C11 (PT49B), R809.2, R810.1
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

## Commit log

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2025-04-27 [kicad] Added schematic
    [acoustic-characterization-hw.kicad_pcb, acoustic-characterization-hw.kicad_sch, inverter.kicad_sch]
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2025-04-27 [simulations] Updated sim with new values [kicad] Added inverter circuitry to schematic, add bulk capacitor LCSC parts, add pads for power connections.
    [inverter.kicad_sch]
2025-04-28 [kicad] Added capacitors, [documentation] Added bootstrap + HF frequency capacitor calculations
    [inverter.kicad_sch]
2025-04-29 [kicad] Added analog front-end schematic and MS9280 symbol
    [acoustic-characterization-hw.kicad_sch, analog_frontend.kicad_sch, processing.kicad_sch]
2025-04-29 [kicad, documentation] Set pin configuration, kept possibility open for reference voltage change and top/bottom, center, differential mode
    [acoustic-characterization-hw.kicad_sch, analog_frontend.kicad_sch]
2025-04-29 [documentation, kicad] Added decoupling capacitors + input circuitry for adc (next) Look for a decent connector
    [analog_frontend.kicad_sch, inverter.kicad_sch]
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2025-05-01 [kicad] Added connector + input circuit (next) Simulate adc input circuit in ltspice
    [analog_frontend.kicad_sch]
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2025-05-04 [kicad] Added initial config and jtag circuitrtry, added kicad symbol, added pinout + script for functionality checking (next) add qspi flash for boot
    [FPGA-SC-02033-2-0-ECP5U-25-Pinout.csv, acoustic-characterization-hw.kicad_sch, analog_frontend.kicad_sch, communication.kicad_sch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]
2025-05-04 [kicad] Added flash memory + flash connection (next) Add RAM and ethernet
    [processing.kicad_sch]
2025-05-05 [kicad] Chose RAM, connecting pins
    [acoustic-characterization-hw.kicad_sch, processing.kicad_sch, ram.kicad_sch]
2025-05-06 [kicad] Connected DDR3L bus, added info on FPGA and ddr pin functionality (next) add filtering circuitry for DDR power pins
    [analog_frontend.kicad_sch, inverter.kicad_sch, power.kicad_sch, processing.kicad_sch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]
2025-05-06 [kicad] re-added passive values after accidental removal
    [analog_frontend.kicad_sch, inverter.kicad_sch, processing.kicad_sch, ram.kicad_sch]
2025-05-06 [simulations] Added buck converter simulations (next) Completely understand voltage swing reasons and stabilize
    [ram.kicad_sch]
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2025-05-06 [kicad] Added switching regulators for 3.3, 1.25 and 2.5
    [power.kicad_sch]
2025-05-07 [general] Major repo reorganization, separated into carrier-board, power-board, preamp-board
    [FPGA-SC-02033-2-0-ECP5U-25-Pinout.csv, acoustic-carrier-board.kicad_pcb, acoustic-carrier-board.kicad_sch, acoustic-characterization-hw.kicad_sch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]
2025-05-08 [acoustic-carrier-board] Added ethernet PHY
    [communication.kicad_sch, processing.kicad_sch]
2025-05-08 [carrier] Same as previous [piezodriver] Moved inverter to separate board
    [acoustic-piezodriver-board.kicad_sch, power.kicad_sch]
2025-05-08 [carrier] Added decoupling for DDR (next) Finish power supply
    [fpga_pinout.csv, inverter.kicad_sch, power.kicad_sch, processing.kicad_sch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]
2025-05-08 [carrier] Finished buck converters + simulations (next) Connect power to FPGA + add decoupling and bulk capacitance
    [power.kicad_sch]
2025-05-08 added decoupling and power flags
    [analog_frontend.kicad_sch, power.kicad_sch, processing.kicad_sch, ram.kicad_sch]
2025-05-09 [carrier] Added space for ferrite bead in between bulk and decoupling caps
    [power.kicad_sch]
2025-05-09 [carrier] Added decoupling to ethernet PHY
    [analog_frontend.kicad_sch, communication.kicad_sch, power.kicad_sch, processing.kicad_sch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]
2025-05-10 [carrier] Finished ethernet
    [acoustic-carrier-board.kicad_sch, analog_frontend.kicad_sch, communication.kicad_sch]
2025-05-10 [carrier] Added usb power + communication circuitry (next) Connect ADC pins to bank 0, select PWM pins, check connectors for power board
    [analog_frontend.kicad_sch, communication.kicad_sch, inverter.kicad_sch, power.kicad_sch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]
2025-05-10 [carrier] Finished basic ADC connections (next) decide on connections with power board
    [analog_frontend.kicad_sch, ram.kicad_sch]
2025-05-11 [carrier] Added adc connections and PWM + poweer connectors
    [analog_frontend.kicad_sch, communication.kicad_sch, power.kicad_sch]
2025-05-11 [piezodriver] Added piezo-driver board connectors
    [inverter.kicad_sch, power.kicad_sch]
2025-05-11 [piezodriver] Changed piezodriver hardware, (next) create simulations in ltspice, pick components
    [power.kicad_sch]
2025-05-12 [piezo-driver] Doing boost converter simulations (next) fix weird transient, add buck-converter simulations for 10 and 5 V
    [acoustic-carrier-board.kicad_pcb]
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2025-05-18 [driver] added components to sepic, added notes
    [inverter.kicad_sch, power.kicad_sch]
2025-05-18 [piezodriver] Added X7R input capacitor, add input and output capacitance of 40-100 uF
    [inverter.kicad_sch, power.kicad_sch]
2025-05-19 [piezodriver] Added input and output capacitor to 10 V sepic
    [power.kicad_sch]
2025-05-19 [piezodriver] Finished 2 sepic designs, starting boost design (warn) Make sure to max diode voltage difference
    [power.kicad_sch]
2025-05-19 [piezodriver] Choose smaller inductor with larger current carrying capacity, increase switching frequency (but check LM3478 limits)
    [power.kicad_sch]
2025-05-20 [piezodriver] Finished boost converter simulation and part selection, working on compensation circuit and control loop
    [power.kicad_sch]
2025-05-20 [piezodriver] Finished boost converter dynamics, added compensation circuitry
    [power.kicad_sch]
2025-05-20 [carrier] Reordered carrier board (next) add magnetics to adc differential and ethernet instead of capacitors - SRF is too low
    [analog_frontend.kicad_sch, fpga_pinout.csv, inverter.kicad_sch, power.kicad_sch]
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2025-05-24 [carrier] Started schematic check, replaced 8 with 16 pin connectors
    [analog_frontend.kicad_sch, communication.kicad_sch, power.kicad_sch, processing.kicad_sch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]
2025-05-25 [carrier] removed external led, using ethernet leds, replaced 1kOhm by 470 ohm resistors
    [analog_frontend.kicad_sch, communication.kicad_sch, power.kicad_sch, processing.kicad_sch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]
2025-05-25 [carrier] Fixed most of the carrier board ERC issues (next) fix BGA ERC issue
    [acoustic-carrier-board.kicad_sch, analog_frontend.kicad_sch, communication.kicad_sch, power.kicad_sch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]
2025-05-25 [carrier] Fixed ERC errors and fpga-footprints (next) ) add extra pin functionality to 2 remaining banks, perform schematic checks
    [acoustic-carrier-board.kicad_sch, analog_frontend.kicad_sch, communication.kicad_sch, fpga_connector.kicad_sch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]
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2025-05-28 [carrier] Fixed differential source impedance at simulation, added chebyshev + butterworth filters
    [analog_frontend.kicad_sch]
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2025-06-02 [carrier] Replaced voltage reference, added extra 0 ohm resistors, added test-connectors for ADC testing
    [adc_connections.kicad_sch, analog_frontend.kicad_sch]
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2025-06-02 [carrier] Fixed ERC issues, added PDn pin connection
    [analog_frontend.kicad_sch]
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2025-06-02 [carrier] Fixed minor symbol errors, added minor routing info (next) continue schematic check
    [adc_connections.kicad_sch, analog_frontend.kicad_sch, communication.kicad_sch, ram.kicad_sch]
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2025-06-03 [piezodriver] Added tina-ti simulation of 10V sepic (next) fix this sim, add power circuitry sim for carrier in tina-ti
    [power.kicad_sch]
2025-06-04 [carrier] Further verification of power board (next) Replace ddr3l reference voltage using TPS51200
    [power.kicad_sch, ram.kicad_sch]
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2025-06-09 [carrier] Reorganized schematic, moPut adc signals in bus, fixed DRC errors (next) recheck ethernet, check usb, add power switch
    [acoustic-carrier-board.kicad_sch, adc_connections.kicad_sch, communication.kicad_sch, fpga_connector.kicad_sch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]
2025-06-10 [carrier] Fixed error in ethernet power supply, separated footprints + symbols into library (next) check whether supply should be DVDDH
    [adc_connections.kicad_sch, communication.kicad_sch, fpga_connector.kicad_sch, power.kicad_sch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]
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2025-06-11 [¢arrier] Fixed busses, added resistive arrays instead of 4x4k7 or 4x10k
    [acoustic-carrier-board.kicad_sch, adc_connections.kicad_sch, communication.kicad_sch, processing.kicad_sch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]
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2025-06-27 [carrier] Progressing on ddr3 routing (next) check all ddr3 signals for errors, start length matching
    [fpga-dqbank-23.kicad_sch]
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2025-07-10 [carrier] Added delayed startup + some traces (next) fix the errors inside the DDR3 routing somehow
    [analog-frontend.kicad_sch, power.kicad_sch]
2025-07-11 [carrier] Corrected most of the DRC errors, a few tens left + respacing DDR3-traces
    [analog-frontend.kicad_sch, fpga-config-flash.kicad_sch]
2025-07-13 [carrier] Fixed most routing errors
    [analog-frontend.kicad_sch]
2025-07-13 [carrier] Fixed last errors, redid length matching for LPDDR3
    [acoustic-carrier-board.kicad_sch]
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
